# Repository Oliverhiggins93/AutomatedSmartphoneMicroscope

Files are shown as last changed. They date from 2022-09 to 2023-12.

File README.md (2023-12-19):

# AutomatedSmartphoneMicroscopeForDiagnosisOfHelminths

This is the github repo corresponding to the PhD thesis of Oliver Higgins "Deep-learning-assisted portable microscopy for disease diagnosis in low-resource settings". 

The project concerns the creation of a smartphone controlled portable microscope, which was used to detect Helminth eggs in faecal smears. The micrscope app includes an EfficientDet-based object detection algorithm which detects the eggs of the six most common spcies of helminth in images.

# Documentation 

Documentation for building the hardware and using the software is available at: https://oliverhiggins93.github.io/AutomatedSmartphoneMicroscope/

# Dataset 

A dataset of over 12,000 images of Helminth eggs was created as part of this project. The dataset includes images taken with standard brightfield microscopes (10x, 20x and 40 objectives) and the portable automated microscope (10x objective). The annotations were made in PASCAL VOC format and confirmed by staff at the Ministry of Health Uganda, Vector Control Division in Kampala. The dataset is available on Kaggle:

Dataset: https://www.kaggle.com/datasets/oliverjackhiggins/helminth-image-dataset

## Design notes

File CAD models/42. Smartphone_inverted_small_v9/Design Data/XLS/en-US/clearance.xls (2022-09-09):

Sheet: Ansi Unified Screw Threads
I | Sort Order -1
Fastener Type | Size | Shaft Diameters |  |  | Head Dimensions
 |  | Close | Normal | Loose | Diameter | Depth/Angle | Head Type
Flat Head Machine Screw (82) | #0 | 0.0635 | 0.07 | 0.073 | 0.119 | 82 | 2
Flat Head Machine Screw (82) | #1 | 0.076 | 0.081 | 0.089 | 0.146 | 82 | 2
Flat Head Machine Screw (82) | #2 | 0.089 | 0.096 | 0.1065 | 0.172 | 82 | 2
Flat Head Machine Screw (82) | #3 | 0.104 | 0.11 | 0.12 | 0.199 | 82 | 2
Flat Head Machine Screw (82) | #4 | 0.116 | 0.1285 | 0.136 | 0.225 | 82 | 2
Flat Head Machine Screw (82) | #5 | 0.1285 | 0.136 | 0.154 | 0.252 | 82 | 2
Flat Head Machine Screw (82) | #6 | 0.144 | 0.1495 | 0.1695 | 0.279 | 82 | 2
Flat Head Machine Screw (82) | #8 | 0.1695 | 0.177 | 0.1935 | 0.332 | 82 | 2
Flat Head Machine Screw (82) | #10 | 0.196 | 0.201 | 0.221 | 0.385 | 82 | 2
Flat Head Machine Screw (82) | #12 | 0.221 | 0.228 | 0.246 | 0.438 | 82 | 2
Flat Head Machine Screw (82) | 1/4 | 0.257 | 0.266 | 0.2812 | 0.507 | 82 | 2
Flat Head Machine Screw (82) | 5/16 | 0.323 | 0.332 | 0.3437 | 0.635 | 82 | 2
Flat Head Machine Screw (82) | 3/8 | 0.386 | 0.397 | 0.4062 | 0.762 | 82 | 2
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

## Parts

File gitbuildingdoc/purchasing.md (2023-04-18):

[M6x130 screws]:Parts.yaml#M3x8PanSteel
[M3x30 screws]:Parts.yaml#M3x8PanSteel
[M3x8 screws]:Parts.yaml#M3x8PanSteel
[M4x10 screws]:Parts.yaml#M4x10PanSteel
[No. 2 Phillips screwdriver]:Parts.yaml#Screwdriver_Philips_No2
[28BYJ-48]:Parts.yaml#28BYJ-48
[ULN2003]:Parts.yaml#ULN2003
[No. 2 Phillips screwdriver]:Parts.yaml#Screwdriver_Philips_No2

# Purchasing parts

The microscope contains quite a few parts which are not printed. The majority of these parts are bolts and motors which can be purchased in sets on Amazon or eBay. Currently there are lots of bolts needed for the microscope - in future iterations the number of bolts may be reduced. 

The Raspberry Pi Zero 2 is currently (as of 2022) difficult to acquire. If you cannot find one, you can get away with using the Raspberry Pi Zero, although the framerate will be slightly slower to stream to the smartphone. 

##Bolts

* [M3x8 bolts]: For fixing the Raspberry Pi, motors and motor boards to the microscope 
* [M4x10 bolts]: For fixing various parts of the stage together
* [M3x30 bolts]: Used for Z-travel
* [M6x130 bolts]: Used for X and Y travel

##Motor electronics
* 3x [28BYJ-48] Stepper motors
* 3x [ULN2003] Motor driver board

##LED electronics
* 1W White Star LED
* 100 Ohm resistor

##Raspberry Pi and camera
* Raspberry Pi HQ camera module
* Raspberry Pi
* 5V Power bank
* USB cable for power bank

##Optics
* 13mm diameter, 5mm focal length plastic condenser lens
* RMS objective
* Achromatic doublet tube lens (optional)

##Smartphone
* This should be any modern Android smartphone

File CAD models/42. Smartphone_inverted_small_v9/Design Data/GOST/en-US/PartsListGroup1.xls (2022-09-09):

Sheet: Лист 1
Инв. № подл |  |  |  | Подп. и дата | Взам. инв. № | Инв. № дубл. |  |  | Подп. и дата
Формат | Зона | Поз. | Обозначение |  |  |  | Наименование |  |  |  |  |  | Кол. на исполнение
 |  |  |  |  |  |  |  |  |  |  |  | Лит.
 |  |  |  |  |  |  |  |  |  |  |  | Код
 |  |  |  |  |  |  |  | Изм. | Лист | № докум | Подпись |  | Дата
 |  |  |  |  |  |  |  | Разраб.
 |  |  |  |  |  |  |  | Пров.
 |  |  |  |  |  |  |  | Н.контр
 |  |  |  |  |  |  |  | Утв.
 |  |  |  |  |  |  |  |  |  |  |  |  |  | Копировал

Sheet: Лист 2
Инв. № подл |  |  |  | Подп. и дата | Взам. инв. № | Инв. № дубл. |  |  | Подп. и дата
Формат | Зона | Поз. | Обозначение |  |  |  | Наименование |  |  |  |  | Кол. на исполнение
 |  |  |  |  |  |  |  | Изм. | Лист | № докум. | Подп. | Дата
 |  |  |  |  |  |  |  |  |  |  |  |  | Копировал
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

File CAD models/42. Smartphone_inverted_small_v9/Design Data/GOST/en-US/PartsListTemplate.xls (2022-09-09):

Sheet: Лист 1
 | Формат | Зона |  | Поз. |  | Обозначение |  |  |  | Наименование |  |  |  | Кол. | Приме-чание
Подп. и дата
Инв. № дубл.
Взам. инв. №
Подп. и дата
 | Изм. |  | Лист |  | № докум |  | Подпись | Дата
Инв. № подл | Разраб. |  |  |  |  |  |  |  |  |  | Литера |  | Лист |  |  | Листов
 | Пров.
 | Н.контр
 | Утв.
 |  |  |  |  |  |  |  |  | Копировал |  |  | Формат А4

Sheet: Лист 2
 | Формат | Зона |  | Поз. |  | Обозначение |  |  |  | Наименование |  | Кол. | Приме-чание
Подп. и дата
Инв. № дубл.
Взам. инв. №
Подп. и дата
Инв. № подл
 | Изм. |  | Лист |  | № докум. |  | Подп. |  | Дата
 |  |  |  |  |  |  |  | Копировал |  |  | Формат А4
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

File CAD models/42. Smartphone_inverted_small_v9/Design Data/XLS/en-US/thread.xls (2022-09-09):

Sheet: Inch Tapping Threads
I Q X | Inch Tapping Threads |  | Sort Order - 5 |  | External |  |  |  |  |  |  | Internal
 |  |  |  |  |  | Major Dia |  | Pitch Dia |  | Minor Dia |  |  | Minor Dia |  | Pitch Dia |  | Major Dia |  | Tap Drill
Size | Size Suffix | Thread Designation | Custom Thread Designation | TPI | Class | Max | Min | Max | Min | Max | Min | Class | Min | Max | Min | Max | Min | Max | Basic
0.0600 |  | 0-48 | 0-48 | 48 | 2B | 0.0600 | 0.0540 | 0.0480 | 0.0435 | 0.0360 | 0.0330
0.0730 |  | 1-42 | 1-42 | 42 | 2B | 0.0750 | 0.0690 | 0.0620 | 0.0575 | 0.0490 | 0.0460
0.0860 |  | 2-32 | 2-32 | 32 | 2B | 0.0880 | 0.0820 | 0.0760 | 0.0710 | 0.0640 | 0.0600
0.0990 |  | 3-28 | 3-28 | 28 | 2B | 0.1010 | 0.0950 | 0.0880 | 0.0830 | 0.0750 | 0.0710
0.1120 |  | 4-24 | 4-24 | 24 | 2B | 0.1140 | 0.1080 | 0.1000 | 0.0950 | 0.0860 | 0.0820
0.1250 |  | 5-20 | 5-20 | 20 | 2B | 0.1300 | 0.1230 | 0.1120 | 0.1065 | 0.0940 | 0.0900
0.1380 |  | 6-20 | 6-20 | 20 | 2B | 0.1390 | 0.1320 | 0.1215 | 0.1155 | 0.1040 | 0.0990
0.1510 |  | 7-19 | 7-19 | 19 | 2B | 0.1540 | 0.1470 | 0.1345 | 0.1280 | 0.1150 | 0.1090
0.1640 |  | 8-18 | 8-18 | 18 | 2B | 0.1660 | 0.1590 | 0.1440 | 0.1375 | 0.1220 | 0.1160
0.1900 |  | 10-16 | 10-16 | 16 | 2B | 0.1890 | 0.1820 | 0.1650 | 0.1585 | 0.1410 | 0.1350
0.2160 |  | 12-14 | 12-14 | 14 | 2B | 0.2150 | 0.2080 | 0.1895 | 0.1825 | 0.1640 | 0.1570
0.2420 |  | 14-14 | 14-14 | 14 | 2B | 0.2410 | 0.2340 | 0.2130 | 0.2060 | 0.1850 | 0.1780
0.2500 |  | 1/4-14 | 1/4-14 | 14 | 2B | 0.2460 | 0.2370 | 0.2190 | 0.2110 | 0.1920 | 0.1850
0.3125 |  | 5/16-12 | 5/16-12 | 12 | 2B | 0.3150 | 0.3060 | 0.2795 | 0.2710 | 0.2440 | 0.2360
0.3750 |  | 3/8-12 | 3/8-12 | 12 | 2B | 0.3800 | 0.3710 | 0.3445 | 0.3350 | 0.3090 | 0.2990
0.4375 |  | 7/16-10 | 7/16-10 | 10 | 2B | 0.4400 | 0.4290 | 0.3995 | 0.3890 | 0.3590 | 0.3490
0.5000 |  | 1/2-10 | 1/2-10 | 10 | 2B | 0.5040 | 0.4930 | 0.4635 | 0.4530 | 0.4230 | 0.4130

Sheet: Metric Forming Screw Threads
M P X | Metric Forming Screw Threads |  | Sort Order - 6 |  | External |  |  |  |  |  |  | Internal
 |  |  |  |  |  | Major Dia |  | Pitch Dia |  | Minor Dia |  |  | Minor Dia |  | Pitch Dia |  | Major Dia |  | Tap Drill
Size | Size Suffix | Thread Designation | Custom Thread Designation | Pitch | Class | Max | Min | Max | Min | Max | Min | Class | Min | Max | Min | Max | Min | Max | Basic
1.5 |  | 1.5x0.5 | 1.5x0.5 | 0.5 | 6g | 1.520 | 1.380 | 1.215 | 1.110 | 0.910 | 0.840
1.5 |  | ST1.5x0.5 | ST1.5x0.5 | 0.5 | 6g | 1.520 | 1.380 | 1.215 | 1.110 | 0.910 | 0.840
1.9 |  | 1.9x0.6 | 1.9x0.6 | 0.6 | 6g | 1.900 | 1.760 | 1.570 | 1.465 | 1.240 | 1.170
1.9 |  | ST1.9x0.6 | ST1.9x0.6 | 0.6 | 6g | 1.900 | 1.760 | 1.570 | 1.465 | 1.240 | 1.170
2.2 |  | 2.2x0.8 | 2.2x0.8 | 0.8 | 6g | 2.240 | 2.100 | 1.935 | 1.810 | 1.630 | 1.520
2.2 |  | ST2.2x0.8 | ST2.2x0.8 | 0.8 | 6g | 2.240 | 2.100 | 1.935 | 1.810 | 1.630 | 1.520
2.6 |  | 2.6x0.9 | 2.6x0.9 | 0.9 | 6g | 2.570 | 2.430 | 2.235 | 2.115 | 1.900 | 1.800
2.6 |  | ST2.6x0.9 | ST2.6x0.9 | 0.9 | 6g | 2.570 | 2.430 | 2.235 | 2.115 | 1.900 | 1.800
2.9 |  | 2.9x1 | 2.9x1 | 1 | 6g | 2.900 | 2.760 | 2.540 | 2.420 | 2.180 | 2.080
2.9 |  | 2.9x1.1 | 2.9x1.1 | 1.1 | 6g | 2.900 | 2.760 | 2.540 | 2.420 | 2.180 | 2.080
2.9 |  | ST2.9x1.1 | ST2.9x1.1 | 1.1 | 6g | 2.900 | 2.760 | 2.540 | 2.420 | 2.180 | 2.080
2.9 |  | 2.9x1.3 | 2.9x1.3 | 1.3 | 6g | 2.900 | 2.720 | 2.540 | 2.355 | 1.890 | 1.700
2.9 |  | 2.9x1.4 | 2.9x1.4 | 1.4 | 6g | 2.900 | 2.720 | 2.340 | 2.175 | 1.780 | 1.630
3.3 |  | 3.3x1.3 | 3.3x1.3 | 1.3 | 6g | 3.300 | 3.120 | 2.795 | 2.665 | 2.290 | 2.210
3.3 |  | ST3.3x1.3 | ST3.3x1.3 | 1.3 | 6g | 3.300 | 3.120 | 2.795 | 2.665 | 2.290 | 2.210
3.5 |  | 3.5x1.3 | 3.5x1.3 | 1.3 | 6g | 3.530 | 3.350 | 3.085 | 2.930 | 2.640 | 2.510
3.5 |  | ST3.5x1.3 | ST3.5x1.3 | 1.3 | 6g | 3.530 | 3.350 | 3.085 | 2.930 | 2.640 | 2.510
3.5 |  | 3.5x1.6 | 3.5x1.6 | 1.6 | 6g | 3.530 | 3.350 | 2.920 | 2.755 | 2.310 | 2.160
3.5 |  | 3.5x3.2 | 3.5x3.2 | 3.2 | 6g | 3.530 | 3.310 | 2.800 | 2.600 | 2.070 | 1.890
3.9 |  | 3.9x1.3 | 3.9x1.3 | 1.3 | 6g | 3.910 | 3.730 | 3.415 | 3.250 | 2.920 | 2.770
3.9 |  | ST3.9x1.3 | ST3.9x1.3 | 1.3 | 6g | 3.910 | 3.730 | 3.415 | 3.250 | 2.920 | 2.770
3.9 |  | 3.9x1.6 | 3.9x1.6 | 1.6 | 6g | 3.910 | 3.730 | 3.300 | 3.135 | 2.690 | 2.540
3.9 |  | 3.9x3.2 | 3.9x3.2 | 3.2 | 6g | 3.910 | 3.690 | 3.180 | 2.980 | 2.450 | 2.270
4.2 |  | 4.2x1.4 | 4.2x1.4 | 1.4 | 6g | 4.220 | 4.040 | 3.660 | 3.495 | 3.100 | 2.950
4.2 |  | ST4.2x1.4 | ST4.2x1.4 | 1.4 | 6g | 4.220 | 4.040 | 3.660 | 3.495 | 3.100 | 2.950
4.2 |  | 4.2x1.6 | 4.2x1.6 | 1.6 | 6g | 4.220 | 4.040 | 3.610 | 3.445 | 3.000 | 2.850
4.2 |  | 4.2x3.2 | 4.2x3.2 | 3.2 | 6g | 4.220 | 4.000 | 3.380 | 3.180 | 2.540 | 2.360
4.8 |  | 4.8x1.6 | 4.8x1.6 | 1.6 | 6g | 4.800 | 4.620 | 4.190 | 4.025 | 3.580 | 3.430
4.8 |  | ST4.8x1.6 | ST4.8x1.6 | 1.6 | 6g | 4.800 | 4.620 | 4.190 | 4.025 | 3.580 | 3.430
4.8 |  | 4.8x1.8 | 4.8x1.8 | 1.8 | 6g | 4.800 | 4.620 | 4.065 | 3.885 | 3.330 | 3.150
4.8 |  | 4.8x3.2 | 4.8x3.2 | 3.2 | 6g | 4.800 | 4.580 | 3.960 | 3.760 | 3.120 | 2.940
5.5 |  | 5.5x1.8 | 5.5x1.8 | 1.8 | 6g | 5.460 | 5.280 | 4.815 | 4.635 | 4.170 | 3.990
5.5 |  | ST5.5x1.8 | ST5.5x1.8 | 1.8 | 6g | 5.460 | 5.280 | 4.815 | 4.635 | 4.170 | 3.990
6.3 |  | 6.3x1.8 | 6.3x1.8 | 1.8 | 6g | 6.250 | 6.030 | 5.565 | 5.365 | 4.880 | 4.700
6.3 |  | ST6.3x1.8 | ST6.3x1.8 | 1.8 | 6g | 6.250 | 6.030 | 5.565 | 5.365 | 4.880 | 4.700
8.0 |  | 8x2.1 | 8x2.1 | 2.1 | 6g | 8.000 | 7.780 | 7.100 | 6.885 | 6.200 | 5.990
8.0 |  | ST8x2.1 | ST8x2.1 | 2.1 | 6g | 8.000 | 7.780 | 7.100 | 6.885 | 6.200 | 5.990
9.5 |  | 9.5x2.1 | 9.5x2.1 | 2.1 | 6g | 9.650 | 9.430 | 8.750 | 8.510 | 7.850 | 7.590
9.5 |  | ST9.5x2.1 | ST9.5x2.1 | 2.1 | 6g | 9.650 | 9.430 | 8.750 | 8.510 | 7.850 | 7.590

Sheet: ISO Pipe Threads
M Q | ISO Pipe Threads |  | Sort Order - 9 |  | External |  |  |  |  |  |  | Internal
 |  |  |  |  |  | Major Dia |  | Pitch Dia |  | Minor Dia |  |  | Minor Dia |  | Pitch Dia |  | Major Dia |  | Tap Drill | Thread Depth | Thread Runouts
Size | Size Suffix | Thread Designation | Custom Thread Designation | TPI | Class | Max | Min | Max | Min | Max | Min | Class | Min | Max | Min | Max | Min | Max | Basic
7.723 |  | G7.723x0.907 | G 1/16 | 28 | A | 7.723 | 7.509 | 7.142 | 7.035 | 6.561 |  |  | 6.561 | 6.834 | 7.142 | 7.249 | 7.723 |  | 1.5875 | 15.446 | 4.5000
7.723 |  | G7.723x0.907 | G 1/16 | 28 | B | 7.723 | 7.509 | 7.142 | 6.928 | 6.561
9.728 |  | G9.728x0.907 | G 1/8 | 28 | A | 9.728 | 9.514 | 9.147 | 9.040 | 8.566 |  |  | 8.566 | 8.848 | 9.147 | 9.254 | 9.728 |  | 3.1750 | 19.456 | 4.5000
9.728 |  | G9.728x0.907 | G 1/8 | 28 | B | 9.728 | 9.514 | 9.147 | 8.933 | 8.566
13.157 |  | G13.157x1.337 | G 1/4 | 19 | A | 13.157 | 12.907 | 12.301 | 12.176 | 11.445 |  |  | 11.445 | 11.89 | 12.301 | 12.426 | 13.157 |  | 6.3500 | 26.314 | 6.5000
13.157 |  | G13.157x1.337 | G 1/4 | 19 | B | 13.157 | 12.907 | 12.301 | 12.051 | 11.445
16.662 |  | G16.662x1.337 | G 3/8 | 19 | A | 16.662 | 16.412 | 15.806 | 15.681 | 14.950 |  |  | 14.95 | 15.395 | 15.806 | 15.931 | 16.662 |  | 9.5250 | 33.324 | 6.5000
16.662 |  | G16.662x1.337 | G 3/8 | 19 | B | 16.662 | 16.412 | 15.806 | 15.556 | 14.950
20.955 |  | G20.955x1.814 | G 1/2 | 14 | A | 20.955 | 20.671 | 19.793 | 19.651 | 18.631 |  |  | 18.631 | 19.172 | 19.793 | 19.935 | 20.955 |  | 12.7000 | 41.910 | 8.5000
20.955 |  | G20.955x1.814 | G 1/2 | 14 | B | 20.955 | 20.671 | 19.793 | 19.509 | 18.631
22.911 |  | G22.911x1.814 | G 5/8 | 14 | A | 22.911 | 22.627 | 21.749 | 21.607 | 20.587 |  |  | 20.587 | 21.128 | 21.749 | 21.891 | 22.911 |  |  | 45.822 | 8.5000
22.911 |  | G22.911x1.814 | G 5/8 | 14 | B | 22.911 | 22.627 | 21.749 | 21.465 | 20.587
26.441 |  | G26.441x1.814 | G 3/4 | 14 | A | 26.441 | 26.157 | 25.279 | 25.137 | 24.117 |  |  | 24.117 | 24.658 | 25.279 | 25.421 | 26.441 |  | 15.8750 | 52.882 | 8.5000
26.441 |  | G26.441x1.814 | G 3/4 | 14 | B | 26.441 | 26.157 | 25.279 | 24.995 | 24.117
30.201 |  | G30.201x1.814 | G 7/8 | 14 | A | 30.201 | 29.917 | 29.039 | 28.897 | 27.877 |  |  | 27.877 | 28.418 | 29.039 | 29.181 | 30.201 |  | 22.2250 | 60.402 | 8.5000
30.201 |  | G30.201x1.814 | G 7/8 | 14 | B | 30.201 | 29.917 | 29.039 | 28.755 | 27.877
33.249 |  | G33.249x2.309 | G 1 | 11 | A | 33.249 | 32.889 | 31.770 | 31.590 | 30.291 |  |  | 30.291 | 30.931 | 31.77 | 31.95 | 33.249 |  | 25.4000 | 66.498 | 10.0000
33.249 |  | G33.249x2.309 | G 1 | 11 | B | 33.249 | 32.889 | 31.770 | 31.410 | 30.291
37.897 |  | G37.897x2.309 | G 1 1/8 | 11 | A | 37.897 | 37.537 | 36.418 | 36.238 | 34.939 |  |  | 34.939 | 35.579 | 36.418 | 36.598 | 37.897 |  | 28.5750 | 75.794 | 10.0000
37.897 |  | G37.897x2.309 | G 1 1/8 | 11 | B | 37.897 | 37.537 | 36.418 | 36.058 | 34.939
41.910 |  | G41.91x2.309 | G 1 1/4 | 11 | A | 41.910 | 41.550 | 40.431 | 40.251 | 38.952 |  |  | 38.952 | 39.592 | 40.431 | 40.611 | 41.910 |  | 31.7500 | 83.820 | 10.0000
41.910 |  | G41.91x2.309 | G 1 1/4 | 11 | B | 41.910 | 41.550 | 40.431 | 40.071 | 38.952
47.803 |  | G47.803x2.309 | G 1 1/2 | 11 | A | 47.803 | 47.443 | 46.324 | 46.144 | 44.845 |  |  | 44.845 | 45.485 | 46.324 | 46.504 | 47.803 |  | 38.1000 | 95.606 | 10.0000
47.803 |  | G47.803x2.309 | G 1 1/2 | 11 | B | 47.803 | 47.443 | 46.324 | 45.964 | 44.845
53.746 |  | G53.746x2.309 | G 1 3/4 | 11 | A | 53.746 | 53.386 | 52.267 | 52.087 | 50.788 |  |  | 50.788 | 51.428 | 52.267 | 52.447 | 53.746 |  | 44.4500 | 107.492 | 10.0000
53.746 |  | G53.746x2.309 | G 1 3/4 | 11 | B | 53.746 | 53.386 | 52.267 | 51.907 | 50.788
59.614 |  | G59.614x2.309 | G 2 | 11 | A | 59.614 | 59.254 | 58.135 | 57.955 | 56.656 |  |  | 56.656 | 57.296 | 58.135 | 58.315 | 59.614 |  | 50.8000 | 119.228 | 10.0000
59.614 |  | G59.614x2.309 | G 2 | 11 | B | 59.614 | 59.254 | 58.135 | 57.775 | 56.656
65.710 |  | G65.71x2.309 | G 2 1/4 | 11 | A | 65.710 | 65.276 | 64.231 | 64.014 | 62.752 |  |  | 62.752 | 63.392 | 64.231 | 64.448 | 65.710 |  | 57.1500 | 131.420 | 10.0000
65.710 |  | G65.71x2.309 | G 2 1/4 | 11 | B | 65.710 | 65.276 | 64.231 | 63.797 | 62.752
75.184 |  | G75.184x2.309 | G 2 1/2 | 11 | A | 75.184 | 74.750 | 73.705 | 73.488 | 72.226 |  |  | 72.226 | 72.866 | 73.705 | 73.922 | 75.184 |  |  | 150.368 | 10.0000
75.184 |  | G75.184x2.309 | G 2 1/2 | 11 | B | 75.184 | 74.750 | 73.705 | 73.271 | 72.226
81.534 |  | G81.534x2.309 | G 2 3/4 | 11 | A | 81.534 | 81.100 | 80.055 | 79.838 | 78.576 |  |  | 78.576 | 79.216 | 80.055 | 80.272 | 81.534 |  | 69.8500 | 163.068 | 10.0000
81.534 |  | G81.534x2.309 | G 2 3/4 | 11 | B | 81.534 | 81.100 | 80.055 | 79.621 | 78.576
87.884 |  | G87.884x2.309 | G 3 | 11 | A | 87.884 | 87.450 | 86.405 | 86.188 | 84.926 |  |  | 84.926 | 85.566 | 86.405 | 86.622 | 87.884 |  | 76.2000 | 175.768 | 10.0000
87.884 |  | G87.884x2.309 | G 3 | 11 | B | 87.884 | 87.450 | 86.405 | 85.971 | 84.926
100.330 |  | G100.33x2.309 | G 3 1/2 | 11 | A | 100.330 | 99.896 | 98.851 | 98.634 | 97.372 |  |  | 97.372 | 98.012 | 98.851 | 99.068 | 100.330 |  | 88.9000 | 200.660 | 10.0000
100.330 |  | G100.33x2.309 | G 3 1/2 | 11 | B | 100.330 | 99.896 | 98.851 | 98.417 | 97.372
113.030 |  | G113.03x2.309 | G 4 | 11 | A | 113.030 | 112.596 | 111.551 | 111.334 | 110.072 |  |  | 110.072 | 110.712 | 111.551 | 111.768 | 113.030 |  | 101.6000 | 226.060 | 10.0000
113.030 |  | G113.03x2.309 | G 4 | 11 | B | 113.030 | 112.596 | 111.551 | 111.117 | 110.072
125.730 |  | G125.73x2.309 | G 4 1/2 | 11 | A | 125.730 | 125.296 | 124.251 | 124.034 | 122.772 |  |  | 122.772 | 123.412 | 124.251 | 124.468 | 125.730 |  | 114.3000 | 251.460 | 10.0000
125.730 |  | G125.73x2.309 | G 4 1/2 | 11 | B | 125.730 | 125.296 | 124.251 | 123.817 | 122.772
138.430 |  | G138.43x2.309 | G 5 | 11 | A | 138.430 | 137.996 | 136.951 | 136.734 | 135.472 |  |  | 135.472 | 136.112 | 136.951 | 137.168 | 138.430 |  | 127.0000 | 276.860 | 10.0000
138.430 |  | G138.43x2.309 | G 5 | 11 | B | 138.430 | 137.996 | 136.951 | 136.517 | 135.472
151.130 |  | G151.13x2.309 | G 5 1/2 | 11 | A | 151.130 | 150.696 | 149.651 | 149.434 | 148.172 |  |  | 148.172 | 148.812 | 149.651 | 149.868 | 151.130 |  | 139.7000 | 302.260 | 10.0000
151.130 |  | G151.13x2.309 | G 5 1/2 | 11 | B | 151.130 | 150.696 | 149.651 | 149.217 | 148.172
163.830 |  | G163.83x2.309 | G 6 | 11 | A | 163.830 | 163.396 | 162.351 | 162.134 | 160.872 |  |  | 160.872 | 161.512 | 162.351 | 162.568 | 163.830 |  | 152.4000 | 327.660 | 10.0000
163.830 |  | G163.83x2.309 | G 6 | 11 | B | 163.830 | 163.396 | 162.351 | 161.917 | 160.872

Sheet: JIS Pipe Threads
M Q | JIS Pipe Threads |  | Sort Order -12 |  | External |  |  |  |  |  |  | Internal
 |  |  |  |  |  | Major Dia |  | Pitch Dia |  | Minor Dia |  |  | Minor Dia |  | Pitch Dia |  | Major Dia |  | Tap Drill | Thread Depth | Thread Runouts
Size | Size Suffix | Thread Designation | Custom Thread Designation | TPI | Class | Max | Min | Max | Min | Max | Min | Class | Min | Max | Min | Max | Min | Max | Basic |  | Basic
7.723 |  | G7.723x0.907 | G 1/16 | 28 | A | 7.723 | 7.509 | 7.142 | 7.035 | 6.561 |  |  | 6.561 | 6.834 | 7.142 | 7.249 | 7.723 |  | 1.5875 | 15.446 | 4.5000
7.723 |  | G7.723x0.907 | G 1/16 | 28 | B | 7.723 | 7.509 | 7.142 | 6.928 | 6.561
9.728 |  | G9.728x0.907 | G 1/8 | 28 | A | 9.728 | 9.514 | 9.147 | 9.040 | 8.566 |  |  | 8.566 | 8.848 | 9.147 | 9.254 | 9.728 |  | 3.1750 | 19.456 | 4.5000
9.728 |  | G9.728x0.907 | G 1/8 | 28 | B | 9.728 | 9.514 | 9.147 | 8.933 | 8.566
13.157 |  | G13.157x1.337 | G 1/4 | 19 | A | 13.157 | 12.907 | 12.301 | 12.176 | 11.445 |  |  | 11.445 | 11.89 | 12.301 | 12.426 | 13.157 |  | 6.3500 | 26.314 | 6.5000
13.157 |  | G13.157x1.337 | G 1/4 | 19 | B | 13.157 | 12.907 | 12.301 | 12.051 | 11.445
16.662 |  | G16.662x1.337 | G 3/8 | 19 | A | 16.662 | 16.412 | 15.806 | 15.681 | 14.950 |  |  | 14.95 | 15.395 | 15.806 | 15.931 | 16.662 |  | 9.5250 | 33.324 | 6.5000
16.662 |  | G16.662x1.337 | G 3/8 | 19 | B | 16.662 | 16.412 | 15.806 | 15.556 | 14.950
20.955 |  | G20.955x1.814 | G 1/2 | 14 | A | 20.955 | 20.671 | 19.793 | 19.651 | 18.631 |  |  | 18.631 | 19.172 | 19.793 | 19.935 | 20.955 |  | 12.7000 | 41.910 | 8.5000
20.955 |  | G20.955x1.814 | G 1/2 | 14 | B | 20.955 | 20.671 | 19.793 | 19.509 | 18.631
22.911 |  | G22.911x1.814 | G 5/8 | 14 | A | 22.911 | 22.627 | 21.749 | 21.607 | 20.587 |  |  | 20.587 | 21.128 | 21.749 | 21.891 | 22.911 |  |  | 45.822 | 8.5000
22.911 |  | G22.911x1.814 | G 5/8 | 14 | B | 22.911 | 22.627 | 21.749 | 21.465 | 20.587
26.441 |  | G26.441x1.814 | G 3/4 | 14 | A | 26.441 | 26.157 | 25.279 | 25.137 | 24.117 |  |  | 24.117 | 24.658 | 25.279 | 25.421 | 26.441 |  | 15.8750 | 52.882 | 8.5000
26.441 |  | G26.441x1.814 | G 3/4 | 14 | B | 26.441 | 26.157 | 25.279 | 24.995 | 24.117
30.201 |  | G30.201x1.814 | G 7/8 | 14 | A | 30.201 | 29.917 | 29.039 | 28.897 | 27.877 |  |  | 27.877 | 28.418 | 29.039 | 29.181 | 30.201 |  | 22.2250 | 60.402 | 8.8000
30.201 |  | G30.201x1.814 | G 7/8 | 14 | B | 30.201 | 29.917 | 29.039 | 28.755 | 27.877
33.249 |  | G33.249x2.309 | G 1 | 11 | A | 33.249 | 32.889 | 31.770 | 31.590 | 30.291 |  |  | 30.291 | 30.931 | 31.77 | 31.95 | 33.249 |  | 25.4000 | 66.498 | 10.0000
33.249 |  | G33.249x2.309 | G 1 | 11 | B | 33.249 | 32.889 | 31.770 | 31.410 | 30.291
37.897 |  | G37.897x2.309 | G 1 1/8 | 11 | A | 37.897 | 37.537 | 36.418 | 36.238 | 34.939 |  |  | 34.939 | 35.579 | 36.418 | 36.598 | 37.897 |  | 28.5750 | 75.794 | 10.0000
37.897 |  | G37.897x2.309 | G 1 1/8 | 11 | B | 37.897 | 37.537 | 36.418 | 36.058 | 34.939
41.910 |  | G41.91x2.309 | G 1 1/4 | 11 | A | 41.910 | 41.550 | 40.431 | 40.251 | 38.952 |  |  | 38.952 | 39.592 | 40.431 | 40.611 | 41.910 |  | 31.7500 | 83.820 | 10.0000
41.910 |  | G41.91x2.309 | G 1 1/4 | 11 | B | 41.910 | 41.550 | 40.431 | 40.071 | 38.952
47.803 |  | G47.803x2.309 | G 1 1/2 | 11 | A | 47.803 | 47.443 | 46.324 | 46.144 | 44.845 |  |  | 44.845 | 45.485 | 46.324 | 46.504 | 47.803 |  | 38.1000 | 95.606 | 10.0000
47.803 |  | G47.803x2.309 | G 1 1/2 | 11 | B | 47.803 | 47.443 | 46.324 | 45.964 | 44.845
53.746 |  | G53.746x2.309 | G 1 3/4 | 11 | A | 53.746 | 53.386 | 52.267 | 52.087 | 50.788 |  |  | 50.788 | 51.428 | 52.267 | 52.447 | 53.746 |  | 44.4500 | 107.492 | 10.0000
53.746 |  | G53.746x2.309 | G 1 3/4 | 11 | B | 53.746 | 53.386 | 52.267 | 51.907 | 50.788
59.614 |  | G59.614x2.309 | G 2 | 11 | A | 59.614 | 59.254 | 58.135 | 57.955 | 56.656 |  |  | 56.656 | 57.296 | 58.135 | 58.315 | 59.614 |  | 50.8000 | 119.228 | 10.0000
59.614 |  | G59.614x2.309 | G 2 | 11 | B | 59.614 | 59.254 | 58.135 | 57.775 | 56.656
65.710 |  | G65.71x2.309 | G 2 1/4 | 11 | A | 65.710 | 65.276 | 64.231 | 64.014 | 62.752 |  |  | 62.752 | 63.392 | 64.231 | 64.448 | 65.710 |  | 57.1500 | 131.420 | 10.0000
65.710 |  | G65.71x2.309 | G 2 1/4 | 11 | B | 65.710 | 65.276 | 64.231 | 63.797 | 62.752
75.184 |  | G75.184x2.309 | G 2 1/2 | 11 | A | 75.184 | 74.750 | 73.705 | 73.488 | 72.226 |  |  | 72.226 | 72.866 | 73.705 | 73.922 | 75.184 |  |  | 150.368 | 10.0000
75.184 |  | G75.184x2.309 | G 2 1/2 | 11 | B | 75.184 | 74.750 | 73.705 | 73.271 | 72.226
81.534 |  | G81.534x2.309 | G 2 3/4 | 11 | A | 81.534 | 81.100 | 80.055 | 79.838 | 78.576 |  |  | 78.576 | 79.216 | 80.055 | 80.272 | 81.534 |  | 69.8500 | 163.068 | 10.0000
81.534 |  | G81.534x2.309 | G 2 3/4 | 11 | B | 81.534 | 81.100 | 80.055 | 79.621 | 78.576
87.884 |  | G87.884x2.309 | G 3 | 11 | A | 87.884 | 87.450 | 86.405 | 86.188 | 84.926 |  |  | 84.926 | 85.566 | 86.405 | 86.622 | 87.884 |  | 76.2000 | 175.768 | 10.0000
87.884 |  | G87.884x2.309 | G 3 | 11 | B | 87.884 | 87.450 | 86.405 | 85.971 | 84.926
100.330 |  | G100.33x2.309 | G 3 1/2 | 11 | A | 100.330 | 99.896 | 98.851 | 98.634 | 97.372 |  |  | 97.372 | 98.012 | 98.851 | 99.068 | 100.330 |  | 88.9000 | 200.660 | 10.0000
100.330 |  | G100.33x2.309 | G 3 1/2 | 11 | B | 100.330 | 99.896 | 98.851 | 98.417 | 97.372
113.030 |  | G113.03x2.309 | G 4 | 11 | A | 113.030 | 112.596 | 111.551 | 111.334 | 110.072 |  |  | 110.072 | 110.712 | 111.551 | 111.768 | 113.030 |  | 101.6000 | 226.060 | 10.0000
113.030 |  | G113.03x2.309 | G 4 | 11 | B | 113.030 | 112.596 | 111.551 | 111.117 | 110.072
125.730 |  | G125.73x2.309 | G 4 1/2 | 11 | A | 125.730 | 125.296 | 124.251 | 124.034 | 122.772 |  |  | 122.772 | 123.412 | 124.251 | 124.468 | 125.730 |  | 114.3000 | 251.460 | 10.0000
125.730 |  | G125.73x2.309 | G 4 1/2 | 11 | B | 125.730 | 125.296 | 124.251 | 123.817 | 122.772
138.430 |  | G138.43x2.309 | G 5 | 11 | A | 138.430 | 137.996 | 136.951 | 136.734 | 135.472 |  |  | 135.472 | 136.112 | 136.951 | 137.168 | 138.430 |  | 127.0000 | 276.860 | 10.0000
138.430 |  | G138.43x2.309 | G 5 | 11 | B | 138.430 | 137.996 | 136.951 | 136.517 | 135.472
151.130 |  | G151.13x2.309 | G 5 1/2 | 11 | A | 151.130 | 150.696 | 149.651 | 149.434 | 148.172 |  |  | 148.172 | 148.812 | 149.651 | 149.868 | 151.130 |  | 139.7000 | 302.260 | 10.0000
151.130 |  | G151.13x2.309 | G 5 1/2 | 11 | B | 151.130 | 150.696 | 149.651 | 149.217 | 148.172
163.830 |  | G163.83x2.309 | G 6 | 11 | A | 163.830 | 163.396 | 162.351 | 162.134 | 160.872 |  |  | 160.872 | 161.512 | 162.351 | 162.568 | 163.830 |  | 152.4000 | 327.660 | 10.0000
163.830 |  | G163.83x2.309 | G 6 | 11 | B | 163.830 | 163.396 | 162.351 | 161.917 | 160.872

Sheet: DIN Pipe Threads
M Q | DIN Pipe Threads |  | Sort Order - 18 |  | External |  |  |  |  |  |  | Internal
 |  |  |  |  |  | Major Dia |  | Pitch Dia |  | Minor Dia |  |  | Minor Dia |  | Pitch Dia |  | Major Dia |  | Tap Drill | Thread Depth | Thread Runouts
Size | Size Suffix | Thread Designation | Custom Thread Designation | TPI | Class | Max | Min | Max | Min | Max | Min | Class | Min | Max | Min | Max | Min | Max | Basic
7.723 |  | G7.723x0.907 | G 1/16 | 28 | A | 7.723 | 7.509 | 7.142 | 7.035 | 6.561 |  |  | 6.561 | 6.834 | 7.142 | 7.249 | 7.723 |  | 1.5875 | 15.446 | 4.5000
7.723 |  | G7.723x0.907 | G 1/16 | 28 | B | 7.723 | 7.509 | 7.142 | 6.928 | 6.561
9.728 |  | G9.728x0.907 | G 1/8 | 28 | A | 9.728 | 9.514 | 9.147 | 9.040 | 8.566 |  |  | 8.566 | 8.848 | 9.147 | 9.254 | 9.728 |  | 3.1750 | 19.456 | 4.5000
9.728 |  | G9.728x0.907 | G 1/8 | 28 | B | 9.728 | 9.514 | 9.147 | 8.933 | 8.566
13.157 |  | G13.157x1.337 | G 1/4 | 19 | A | 13.157 | 12.907 | 12.301 | 12.176 | 11.445 |  |  | 11.445 | 11.89 | 12.301 | 12.426 | 13.157 |  | 6.3500 | 26.314 | 6.5000
13.157 |  | G13.157x1.337 | G 1/4 | 19 | B | 13.157 | 12.907 | 12.301 | 12.051 | 11.445
16.662 |  | G16.662x1.337 | G 3/8 | 19 | A | 16.662 | 16.412 | 15.806 | 15.681 | 14.950 |  |  | 14.95 | 15.395 | 15.806 | 15.931 | 16.662 |  | 9.5250 | 33.324 | 6.5000
16.662 |  | G16.662x1.337 | G 3/8 | 19 | B | 16.662 | 16.412 | 15.806 | 15.556 | 14.950
20.955 |  | G20.955x1.814 | G 1/2 | 14 | A | 20.955 | 20.671 | 19.793 | 19.651 | 18.631 |  |  | 18.631 | 19.172 | 19.793 | 19.935 | 20.955 |  | 12.7000 | 41.910 | 8.5000
20.955 |  | G20.955x1.814 | G 1/2 | 14 | B | 20.955 | 20.671 | 19.793 | 19.509 | 18.631
22.911 |  | G22.911x1.814 | G 5/8 | 14 | A | 22.911 | 22.627 | 21.749 | 21.607 | 20.587 |  |  | 20.587 | 21.128 | 21.749 | 21.891 | 22.911 |  |  | 45.822 | 8.5000
22.911 |  | G22.911x1.814 | G 5/8 | 14 | B | 22.911 | 22.627 | 21.749 | 21.465 | 20.587
26.441 |  | G26.441x1.814 | G 3/4 | 14 | A | 26.441 | 26.157 | 25.279 | 25.137 | 24.117 |  |  | 24.117 | 24.658 | 25.279 | 25.421 | 26.441 |  | 15.8750 | 52.882 | 8.5000
26.441 |  | G26.441x1.814 | G 3/4 | 14 | B | 26.441 | 26.157 | 25.279 | 24.995 | 24.117
30.201 |  | G30.201x1.814 | G 7/8 | 14 | A | 30.201 | 29.917 | 29.039 | 28.897 | 27.877 |  |  | 27.877 | 28.418 | 29.039 | 29.181 | 30.201 |  | 22.2250 | 60.402 | 8.5000
30.201 |  | G30.201x1.814 | G 7/8 | 14 | B | 30.201 | 29.917 | 29.039 | 28.755 | 27.877
33.249 |  | G33.249x2.309 | G 1 | 11 | A | 33.249 | 32.889 | 31.770 | 31.590 | 30.291 |  |  | 30.291 | 30.931 | 31.77 | 31.95 | 33.249 |  | 25.4000 | 66.498 | 10.5000
33.249 |  | G33.249x2.309 | G 1 | 11 | B | 33.249 | 32.889 | 31.770 | 31.410 | 30.291
37.897 |  | G37.897x2.309 | G 1 1/8 | 11 | A | 37.897 | 37.537 | 36.418 | 36.238 | 34.939 |  |  | 34.939 | 35.579 | 36.418 | 36.598 | 37.897 |  | 28.5750 | 75.794 | 10.5000
37.897 |  | G37.897x2.309 | G 1 1/8 | 11 | B | 37.897 | 37.537 | 36.418 | 36.058 | 34.939
41.910 |  | G41.91x2.309 | G 1 1/4 | 11 | A | 41.910 | 41.550 | 40.431 | 40.251 | 38.952 |  |  | 38.952 | 39.592 | 40.431 | 40.611 | 41.910 |  | 31.7500 | 83.820 | 10.5000
41.910 |  | G41.91x2.309 | G 1 1/4 | 11 | B | 41.910 | 41.550 | 40.431 | 40.071 | 38.952
47.803 |  | G47.803x2.309 | G 1 1/2 | 11 | A | 47.803 | 47.443 | 46.324 | 46.144 | 44.845 |  |  | 44.845 | 45.485 | 46.324 | 46.504 | 47.803 |  | 38.1000 | 95.606 | 10.5000
47.803 |  | G47.803x2.309 | G 1 1/2 | 11 | B | 47.803 | 47.443 | 46.324 | 45.964 | 44.845
53.746 |  | G53.746x2.309 | G 1 3/4 | 11 | A | 53.746 | 53.386 | 52.267 | 52.087 | 50.788 |  |  | 50.788 | 51.428 | 52.267 | 52.447 | 53.746 |  | 44.4500 | 107.492 | 10.5000
53.746 |  | G53.746x2.309 | G 1 3/4 | 11 | B | 53.746 | 53.386 | 52.267 | 51.907 | 50.788
59.614 |  | G59.614x2.309 | G 2 | 11 | A | 59.614 | 59.254 | 58.135 | 57.955 | 56.656 |  |  | 56.656 | 57.296 | 58.135 | 58.315 | 59.614 |  | 50.8000 | 119.228 | 10.5000
59.614 |  | G59.614x2.309 | G 2 | 11 | B | 59.614 | 59.254 | 58.135 | 57.775 | 56.656
65.710 |  | G65.71x2.309 | G 2 1/4 | 11 | A | 65.710 | 65.276 | 64.231 | 64.014 | 62.752 |  |  | 62.752 | 63.392 | 64.231 | 64.448 | 65.710 |  | 57.1500 | 131.420 | 10.5000
65.710 |  | G65.71x2.309 | G 2 1/4 | 11 | B | 65.710 | 65.276 | 64.231 | 63.797 | 62.752
75.184 |  | G75.184x2.309 | G 2 1/2 | 11 | A | 75.184 | 74.750 | 73.705 | 73.488 | 72.226 |  |  | 72.226 | 72.866 | 73.705 | 73.922 | 75.184 |  |  | 150.368 | 10.5000
75.184 |  | G75.184x2.309 | G 2 1/2 | 11 | B | 75.184 | 74.750 | 73.705 | 73.271 | 72.226
81.534 |  | G81.534x2.309 | G 2 3/4 | 11 | A | 81.534 | 81.100 | 80.055 | 79.838 | 78.576 |  |  | 78.576 | 79.216 | 80.055 | 80.272 | 81.534 |  | 69.8500 | 163.068 | 10.5000
81.534 |  | G81.534x2.309 | G 2 3/4 | 11 | B | 81.534 | 81.100 | 80.055 | 79.621 | 78.576
87.884 |  | G87.884x2.309 | G 3 | 11 | A | 87.884 | 87.450 | 86.405 | 86.188 | 84.926 |  |  | 84.926 | 85.566 | 86.405 | 86.622 | 87.884 |  | 76.2000 | 175.768 | 10.5000
87.884 |  | G87.884x2.309 | G 3 | 11 | B | 87.884 | 87.450 | 86.405 | 85.971 | 84.926
100.330 |  | G100.33x2.309 | G 3 1/2 | 11 | A | 100.330 | 99.896 | 98.851 | 98.634 | 97.372 |  |  | 97.372 | 98.012 | 98.851 | 99.068 | 100.330 |  | 88.9000 | 200.660 | 10.5000
100.330 |  | G100.33x2.309 | G 3 1/2 | 11 | B | 100.330 | 99.896 | 98.851 | 98.417 | 97.372
113.030 |  | G113.03x2.309 | G 4 | 11 | A | 113.030 | 112.596 | 111.551 | 111.334 | 110.072 |  |  | 110.072 | 110.712 | 111.551 | 111.768 | 113.030 |  | 101.6000 | 226.060 | 10.5000
113.030 |  | G113.03x2.309 | G 4 | 11 | B | 113.030 | 112.596 | 111.551 | 111.117 | 110.072
125.730 |  | G125.73x2.309 | G 4 1/2 | 11 | A | 125.730 | 125.296 | 124.251 | 124.034 | 122.772 |  |  | 122.772 | 123.412 | 124.251 | 124.468 | 125.730 |  | 114.3000 | 251.460 | 10.5000
125.730 |  | G125.73x2.309 | G 4 1/2 | 11 | B | 125.730 | 125.296 | 124.251 | 123.817 | 122.772
138.430 |  | G138.43x2.309 | G 5 | 11 | A | 138.430 | 137.996 | 136.951 | 136.734 | 135.472 |  |  | 135.472 | 136.112 | 136.951 | 137.168 | 138.430 |  | 127.0000 | 276.860 | 10.5000
138.430 |  | G138.43x2.309 | G 5 | 11 | B | 138.430 | 137.996 | 136.951 | 136.517 | 135.472
151.130 |  | G151.13x2.309 | G 5 1/2 | 11 | A | 151.130 | 150.696 | 149.651 | 149.434 | 148.172 |  |  | 148.172 | 148.812 | 149.651 | 149.868 | 151.130 |  | 139.7000 | 302.260 | 10.5000
151.130 |  | G151.13x2.309 | G 5 1/2 | 11 | B | 151.130 | 150.696 | 149.651 | 149.217 | 148.172
163.830 |  | G163.83x2.309 | G 6 | 11 | A | 163.830 | 163.396 | 162.351 | 162.134 | 160.872 |  |  | 160.872 | 161.512 | 162.351 | 162.568 | 163.830 |  | 152.4000 | 327.660 | 10.5000
163.830 |  | G163.83x2.309 | G 6 | 11 | B | 163.830 | 163.396 | 162.351 | 161.917 | 160.872

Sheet: BSP Pipe Threads
M Q | BSP Pipe Threads |  | Sort Order - 19 |  | External |  |  |  |  |  |  | Internal
 |  |  |  |  |  | Major Dia |  | Pitch Dia |  | Minor Dia |  |  | Minor Dia |  | Pitch Dia |  | Major Dia |  | Tap Drill | Thread Depth | Thread Runouts
Size | Size Suffix | Thread Designation | Custom Thread Designation | TPI | Class | Max | Min | Max | Min | Max | Min | Class | Min | Max | Min | Max | Min | Max | Basic |  | Basic
1/16 |  | G 1/16-28 | G 1/16-28 | 28 | A | 7.723 | 7.509 | 7.142 | 7.035 | 6.561 |  |  | 6.561 | 6.834 | 7.142 | 7.249 | 7.723 |  | 6.6000 | 15.4460 | 4.5000
1/16 |  | G 1/16-28 | G 1/16-28 | 28 | B | 7.723 | 7.509 | 7.142 | 7.035 | 6.561
1/8 |  | G 1/8-28 | G 1/8-28 | 28 | A | 9.728 | 9.514 | 9.147 | 9.040 | 8.566 |  |  | 8.566 | 8.848 | 9.147 | 9.254 | 9.728 |  | 8.7300 | 19.4560 | 4.5000
1/8 |  | G 1/8-28 | G 1/8-28 | 28 | B | 9.728 | 9.514 | 9.147 | 9.040 | 8.566
1/4 |  | G 1/4-19 | G 1/4-19 | 19 | A | 13.157 | 12.907 | 12.301 | 12.176 | 11.445 |  |  | 11.445 | 11.89 | 12.301 | 12.426 | 13.157 |  | 11.8000 | 26.3140 | 6.5000
1/4 |  | G 1/4-19 | G 1/4-19 | 19 | B | 13.157 | 12.907 | 12.301 | 12.176 | 11.445
3/8 |  | G 3/8-19 | G 3/8-19 | 19 | A | 16.662 | 16.412 | 15.806 | 15.681 | 14.950 |  |  | 14.95 | 15.395 | 15.806 | 15.931 | 16.662 |  | 15.2500 | 33.3240 | 6.5000
3/8 |  | G 3/8-19 | G 3/8-19 | 19 | B | 16.662 | 16.412 | 15.806 | 15.681 | 14.950
1/2 |  | G 1/2-14 | G 1/2-14 | 14 | A | 20.955 | 20.671 | 19.793 | 19.651 | 18.631 |  |  | 18.631 | 19.172 | 19.793 | 19.935 | 20.955 |  | 19.0500 | 41.9100 | 8.5000
1/2 |  | G 1/2-14 | G 1/2-14 | 14 | B | 20.955 | 20.671 | 19.793 | 19.651 | 18.631
5/8 |  | G 5/8-14 | G 5/8-14 | 14 | A | 22.911 | 22.627 | 21.749 | 21.607 | 20.587 |  |  | 20.587 | 21.128 | 21.749 | 21.891 | 22.911 |  | 21.0000 | 45.8220 | 8.5000
5/8 |  | G 5/8-14 | G 5/8-14 | 14 | B | 22.911 | 22.627 | 21.749 | 21.607 | 20.587
3/4 |  | G 3/4-14 | G 3/4-14 | 14 | A | 26.441 | 26.157 | 25.279 | 25.137 | 24.117 |  |  | 24.117 | 24.658 | 25.279 | 25.421 | 26.441 |  | 24.5000 | 52.8820 | 8.5000
3/4 |  | G 3/4-14 | G 3/4-14 | 14 | B | 26.441 | 26.157 | 25.279 | 25.137 | 24.117
7/8 |  | G 7/8-14 | G 7/8-14 | 14 | A | 30.201 | 29.917 | 29.039 | 28.897 | 27.877 |  |  | 27.877 | 28.418 | 29.039 | 29.181 | 30.201 |  | 28.2500 | 60.4020 | 8.5000
7/8 |  | G 7/8-14 | G 7/8-14 | 14 | B | 30.201 | 29.917 | 29.039 | 28.897 | 27.877
1 |  | G 1-11 | G 1-11 | 11 | A | 33.249 | 32.889 | 31.770 | 31.590 | 30.291 |  |  | 30.291 | 30.931 | 31.77 | 31.95 | 33.249 |  | 30.7500 | 66.4980 | 10.0000
1 |  | G 1-11 | G 1-11 | 11 | B | 33.249 | 32.889 | 31.770 | 31.590 | 30.291
1 1/4 |  | G 1 1/4-11 | G 1 1/4-11 | 11 | A | 41.910 | 41.550 | 40.431 | 40.251 | 38.952 |  |  | 38.952 | 39.592 | 40.431 | 40.611 | 41.910 |  | 39.5000 | 83.8200 | 10.0000
1 1/4 |  | G 1 1/4-11 | G 1 1/4-11 | 11 | B | 41.910 | 41.550 | 40.431 | 40.251 | 38.952
1 1/2 |  | G 1 1/2-11 | G 1 1/2-11 | 11 | A | 47.803 | 47.443 | 46.324 | 46.144 | 44.845 |  |  | 44.845 | 45.485 | 46.324 | 46.504 | 47.803 |  | 45.5000 | 95.6060 | 10.0000
1 1/2 |  | G 1 1/2-11 | G 1 1/2-11 | 11 | B | 47.803 | 47.443 | 46.324 | 46.144 | 44.845
1 3/4 |  | G 1 3/4-11 | G 1 3/4-11 | 11 | A | 53.746 | 53.386 | 52.267 | 52.087 | 50.788 |  |  | 50.788 | 51.428 | 52.267 | 52.447 | 53.746 |  | 51.0000 | 107.4920 | 10.0000
1 3/4 |  | G 1 3/4-11 | G 1 3/4-11 | 11 | B | 53.746 | 53.386 | 52.267 | 52.087 | 50.788
2 |  | G 2-11 | G 2-11 | 11 | A | 59.614 | 59.254 | 58.135 | 57.955 | 56.656 |  |  | 56.656 | 57.296 | 58.135 | 58.315 | 59.614 |  | 57.0000 | 119.2280 | 10.0000
2 |  | G 2-11 | G 2-11 | 11 | B | 59.614 | 59.254 | 58.135 | 57.955 | 56.656
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

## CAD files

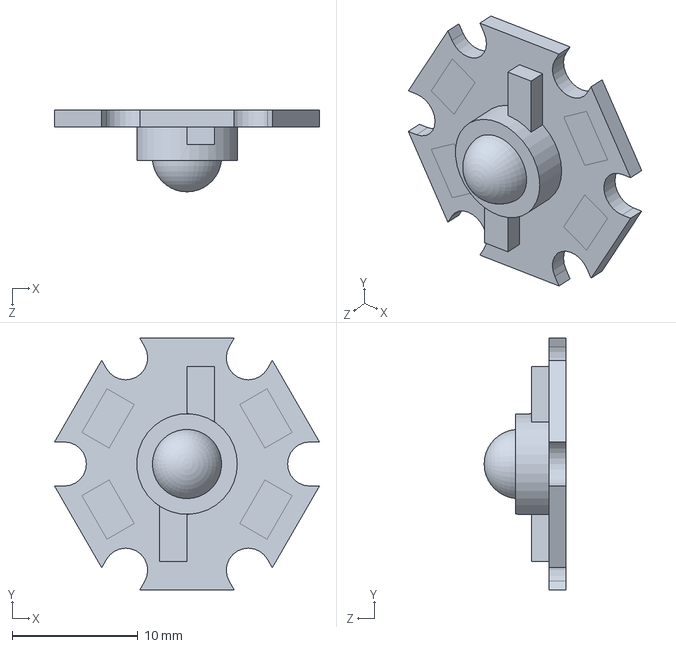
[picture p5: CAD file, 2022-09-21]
CAD models/42. Smartphone_inverted_small_v9/1W_star_LED.SLDPRT
21.1 x 20.0 x 6.50 mm

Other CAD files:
CAD models/42. Smartphone_inverted_small_v9/160mm_shunt_box.ipt
CAD models/42. Smartphone_inverted_small_v9/1W_star_LED.ipt
CAD models/42. Smartphone_inverted_small_v9/28BYJ-48 Stepper.ipt
CAD models/42. Smartphone_inverted_small_v9/3mm_shaft_couple_sideclip_v4.ipt
CAD models/42. Smartphone_inverted_small_v9/6mm_shaft_couple_sideclip_v2.ipt
CAD models/42. Smartphone_inverted_small_v9/AC127-075-A-Step.ipt
CAD models/42. Smartphone_inverted_small_v9/Bottom_carriage.ipt
CAD models/42. Smartphone_inverted_small_v9/Condenser_holder_frame.ipt
CAD models/42. Smartphone_inverted_small_v9/Flexible_cam_holder_v7_HQ.ipt
CAD models/42. Smartphone_inverted_small_v9/Flexible_tube_bolster_fixed_v3.ipt
CAD models/42. Smartphone_inverted_small_v9/Led_frame_2_4mm.ipt
CAD models/42. Smartphone_inverted_small_v9/Lensfree_flexstage_box.iam
CAD models/42. Smartphone_inverted_small_v9/M3 nut.ipt
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

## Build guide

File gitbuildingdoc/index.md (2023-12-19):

# Automated Smartphone Microscope

#Introduction

The following pages provide build and software instructions for the Automated Smartphone Microscope project. This project is a 3D printable microscope which can be controlled using an app installed on any Android smartphone. The microscope is motorised, has a large travel area, and can accept any RMS threaded objective. 

This page provides a few thoughts about the project, while the links below contain information about how to build the microscope and run the software. 

[Github page](https://github.com/Oliverhiggins93/AutomatedSmartphoneMicroscope)

<center>Printed microscope</center>

#Instructions

* [.](introduction.md){step}
* [Bill of materials]{BOM}
* [Purchasing parts](purchasing.md){step}
* [Printing parts](printing.md){step}
* [Assembling microscope](assembly.md){step}
* [Raspberry Pi Software](raspberrypi.md){step}
* [Android Software installation](androidinstallation.md){step}
* [App instructions](appinstructions.md){step}
* [Helminth dataset](dataset.md){step}

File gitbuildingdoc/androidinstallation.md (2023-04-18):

# Android app software

## Pair Raspberry Pi with phone {pagestep}

For starters you will need to make sure that the Raspberry Pi can connect to the smartphone's mobile hotspot. If you used the default SSID and password settings in the previous settings you should only need to change the smartphone's hotspot settings to match the ones that the Raspberry Pi will be expecting to connect to: 

* Network name (SSID) = microscope
* Password = smart 

Usually this can be done through settings. If you search for Mobile Hotspot in your device's search function it will usually take you to a page where you can switch the hotspot on and change the Network name/SSID and password.

You will want to check at this stage that the Raspberry Pi is connected to your mobile hotspot. Usually under the mobile hotspot settings there will be some information telling you which devices are connected. 

## Download Android Studio {pagestep}

Download and install Android Studio from the following website: [Android studio](https://developer.android.com/studio)

## Import app into android studio and install {pagestep}

Open Android Studio once it is downloaded and installed. 

If you have not yet cloned the repository, you will want to do that now using:

> git clone https://github.com/Oliverhiggins93/AutomatedSmartphoneMicroscope.git

In Android Studio, open the project by opening the File dropdown and selection Open 

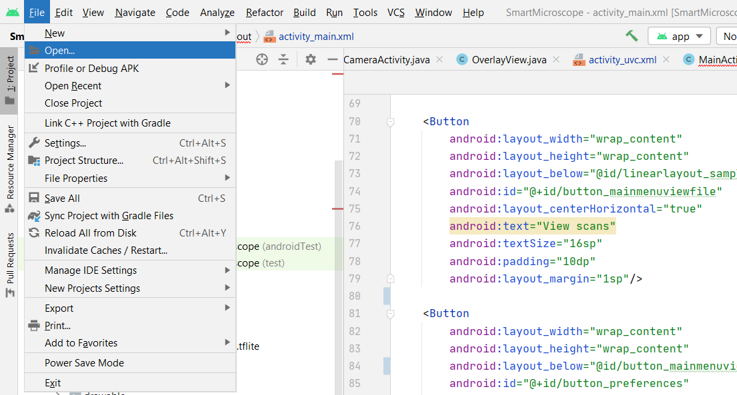
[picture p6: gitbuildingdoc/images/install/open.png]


You will need to open the folder entitled 'Smartmicroscope'.
 
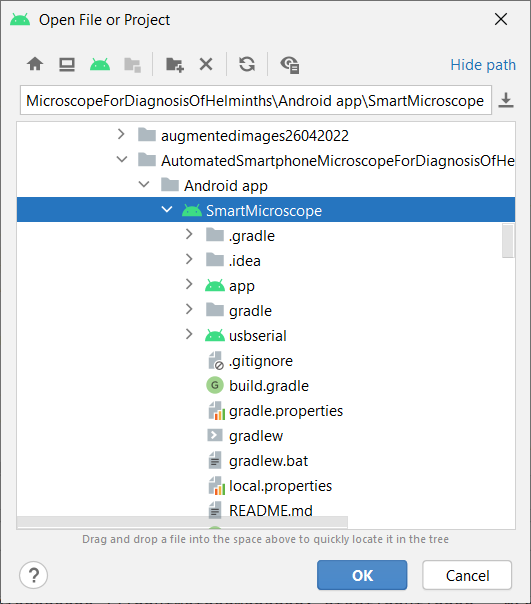
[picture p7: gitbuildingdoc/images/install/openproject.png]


Once this is open you should build and install the app. 

## Run app {pagestep}

You can now run the app from the phone. The most important thing to check at this stage is whether you can receive an image. By clicking on 'Open Web Camera' you should soon begin to see an image stream to your device.

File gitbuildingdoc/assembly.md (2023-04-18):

[Raspberry Pi]:Parts.yaml#RaspberyPi
[Raspberry Pi Camera]:Parts.yaml#RaspberyPiCamera
[M3 bolt]:Parts.yaml#M3x8PanSteel
[28BYJ-48]:Parts.yaml#28BYJ-48
[ULN2003]:Parts.yaml#ULN2003
[Jumper wires]:Parts.yaml#Jumperwires
[3mm bolt coupler]:Parts.yaml#Shaftcouple3mm
[6mm bolt coupler]:Parts.yaml#Shaftcouple6mm
[M3x30mm bolt]:Parts.yaml#M3x30GHexSteel
[M3x8mm bolt]:Parts.yaml#M3x8PanSteel
[M6x130mm bolt]:Parts.yaml#M6x130PanSteel
[M3 nut]:Parts.yaml#M3nut
[M6 nut]:Parts.yaml#M6nut
[M2.5x6mm bolt]:Parts.yaml#M2.5x6
[M4x10mm bolt]:Parts.yaml#M4x10PanSteel
[Condenser lens]:Parts.yaml#Plasticcondenser
[White LED]:Parts.yaml#1WLED
[Resistor]:Parts.yaml#resistor
[RMS objective]:Parts.yaml#rmsobjective
[Tube lens]:Parts.yaml#tubelens
[Camera ribbon]:Parts.yaml#RaspberyPiCameraRibbon

# Assembling the microscope 

## Attaching Raspberry pi and motor drivers to base {pagestep}

We will start by assembling the base of the microscope and attaching the electronic components. You will want to thread the bolts through the bottom of the base so that the threaded ends finish inside the microscopy body. 

Take the [Raspberry Pi]{Qty: 1} and thread an [M3 bolt]{Qty: 4} through the hole in each corners. Secure the [Raspberry Pi] with the bolts and 4x [M3 nut]{Qty: 4}.

Take the 3x [ULN2003]{Qty: 3} motor drivers and attach these to the base in the same way with the [M3 bolt]{Qty: 12}s. Secure with [M3 nut]{Qty: 12}.

Using 2x [M3 bolt]{Qty: 2} attach the [28BYJ-48]{Qty: 1} by screwing bolts through the arms into the plastic holders. Secure with [M3 nut]{Qty: 2}.

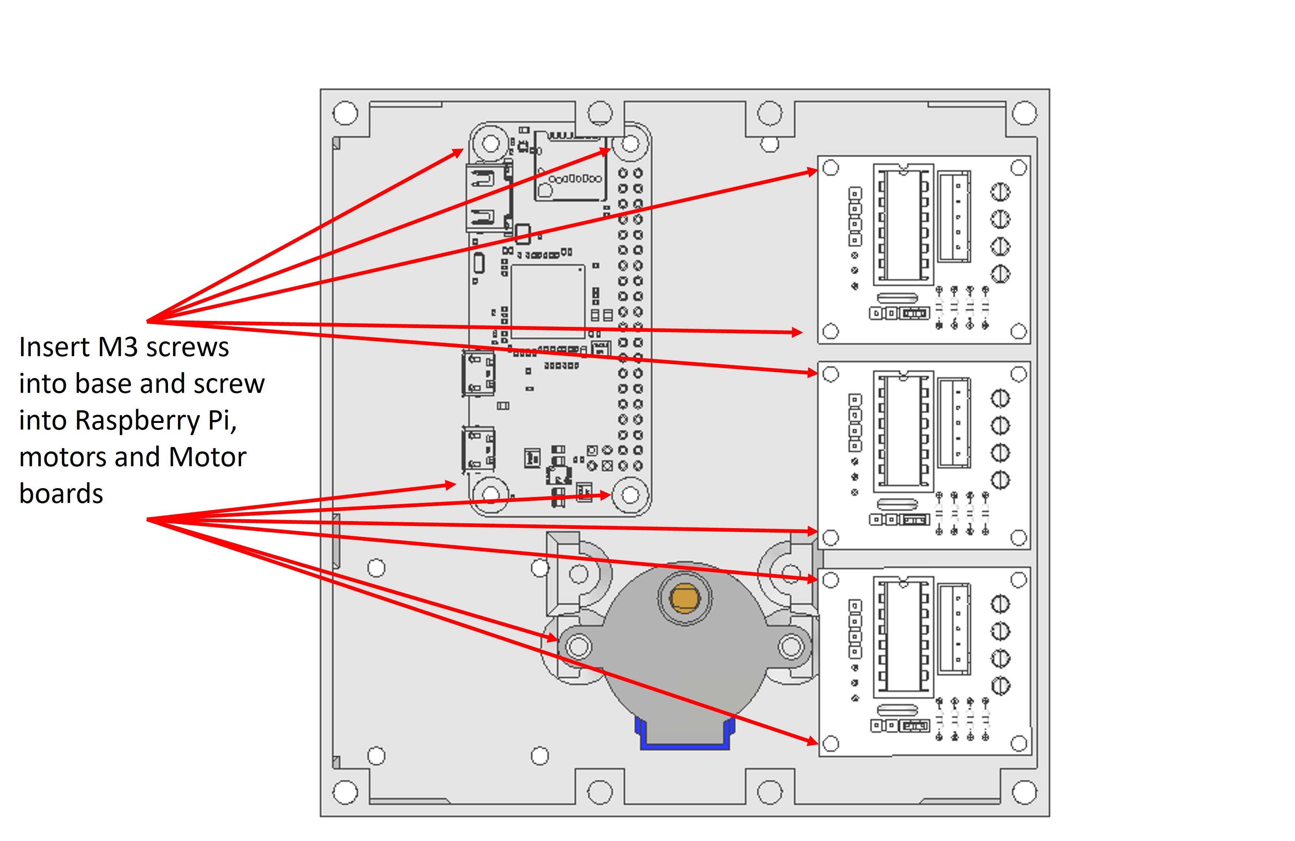
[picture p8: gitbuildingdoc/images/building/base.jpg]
Base instructions


## Motor and motor driver wiring {pagestep}

Attach each [28BYJ-48] header clip to the corresponding [ULN2003] motor driver.

We have had good success powering all of the motors using a simple parallel circuit from the 5V Raspberry Pi pin. Some resources online caution against this, due to concerns that the motors may drain more current than the 5V pin is rated to supply, but personally I have never found any difficulties with this, and it removes the requirement for an additional power source. 

Using [Jumper wires]{Qty: 12} attach each pin of the [ULN2003] to the [Raspberry Pi]. The pin order should be as follows:

* X axis:
    * **Motor pin 1**: Raspberry Pi pin 18
    * **Motor pin 2**: Raspberry Pi pin 23
    * **Motor pin 3**: Raspberry Pi pin 24
    * **Motor pin 4**: Raspberry Pi pin 25

* Y axis:
    * **Motor pin 1**: Raspberry Pi pin 8
    * **Motor pin 2**: Raspberry Pi pin 7
    * **Motor pin 3**: Raspberry Pi pin 12
    * **Motor pin 4**: Raspberry Pi pin 16

* Z axis:
    * **Motor pin 1**: Raspberry Pi pin 4
    * **Motor pin 2**: Raspberry Pi pin 17
    * **Motor pin 3**: Raspberry Pi pin 27
    * **Motor pin 4**: Raspberry Pi pin 22

Please note, if your motors do not move when you test them, you should try to swap motor pin 2 and 3 for each driver. 

## Attaching screw couplings to motors {pagestep}

There are three screw couples; 2x [6mm bolt coupler]{Qty:2} and 1x [3mm bolt coupler]{Qty:1} which are used to attach the [M3x30mm bolt]{Qty:1} and M6 bolts to the [28BYJ-48] motors.

To assemble the screw couplings you should first screw a spare nut all the way along the length of the screw, so that it is flush (or close to flush) with the hex head. You can then insert the hex head into the hexagonal hole in the screw coupler. The nut will help the screw to stay in place in the coupler. 

You can then push the shaft of the [28BYJ-48]{Qty: 2} into the rectangular hole of the screw coupler. 

Once these steps have been completed you should insert 2x [M3 bolt]{Qty:2} into the holes in the side to secure the bolt and shaft from moving. Secure with [M3 nut]{Qty: 2}.

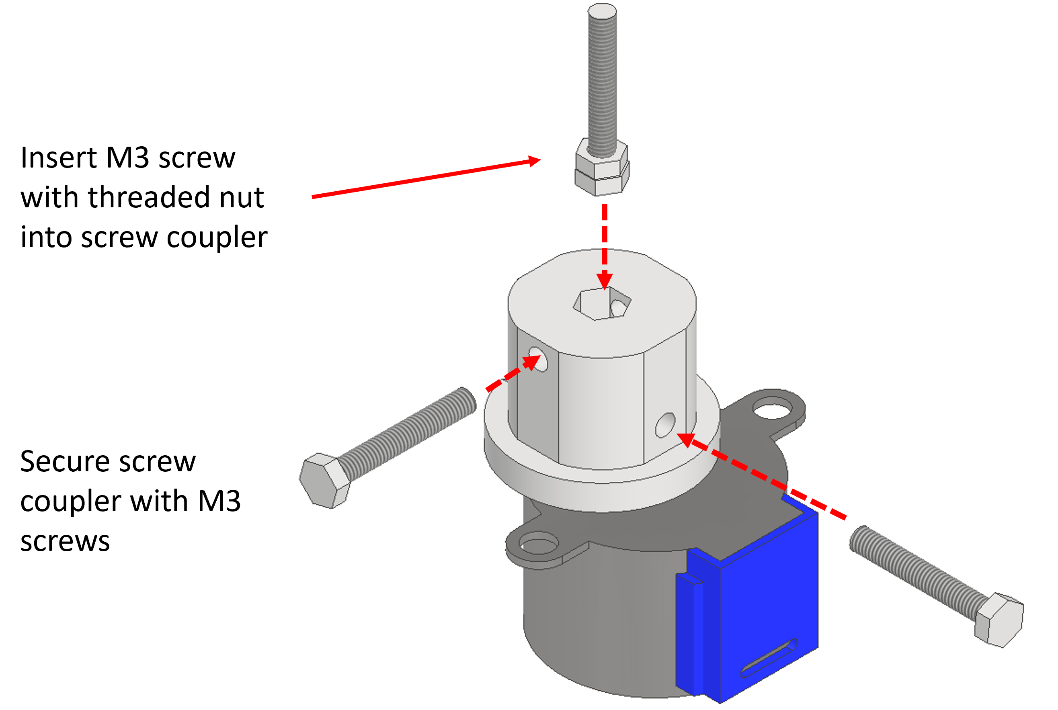
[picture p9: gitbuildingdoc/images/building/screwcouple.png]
Screw coupler


## Assembling Z stage {pagestep}

Insert an [M3 nut]{Qty: 1} into the flexible camera holder. 

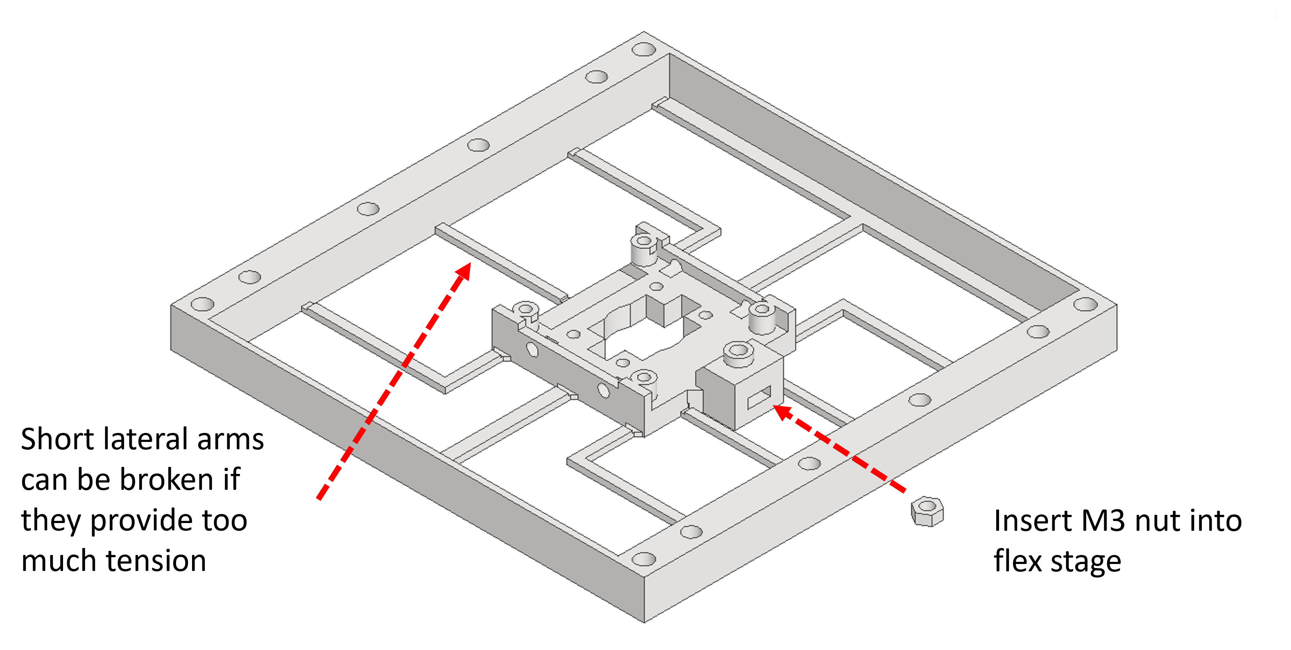
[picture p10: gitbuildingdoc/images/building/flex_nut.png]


## Attaching camera to Z stage {pagestep}

Using 4x [M2.5x6mm bolt]{Qty: 4} Screw the camera onto the flexible holder.

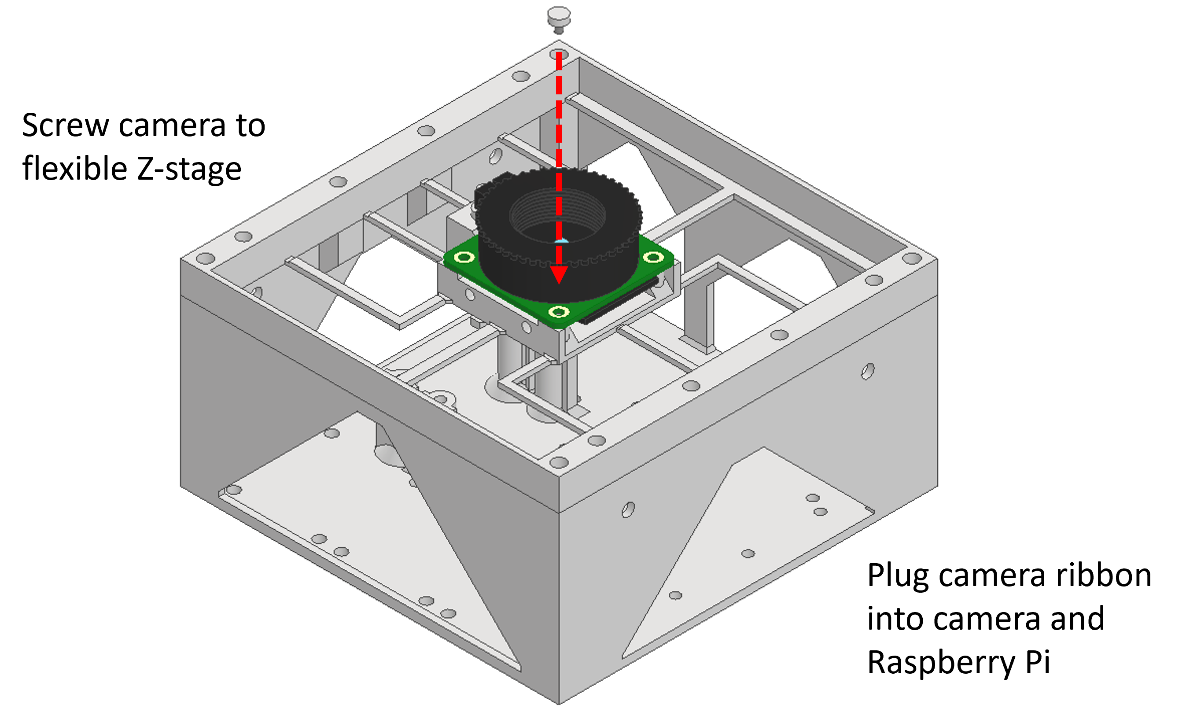
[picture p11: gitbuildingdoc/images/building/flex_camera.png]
Camera holder


You will now need to attach the [Camera ribbon]{Qty: 1}. One end of the camera ribbon will attach to the Raspberry Pi Zero, and the other end will attach to the camera.

## Attaching frame and Z stage to base {pagestep}

Use 4x [M4x10mm bolt]{Qty: 4} to attach the frame to the base. The bolts should screw through the four central holes in the frame, through the camera holder, and into the base. 

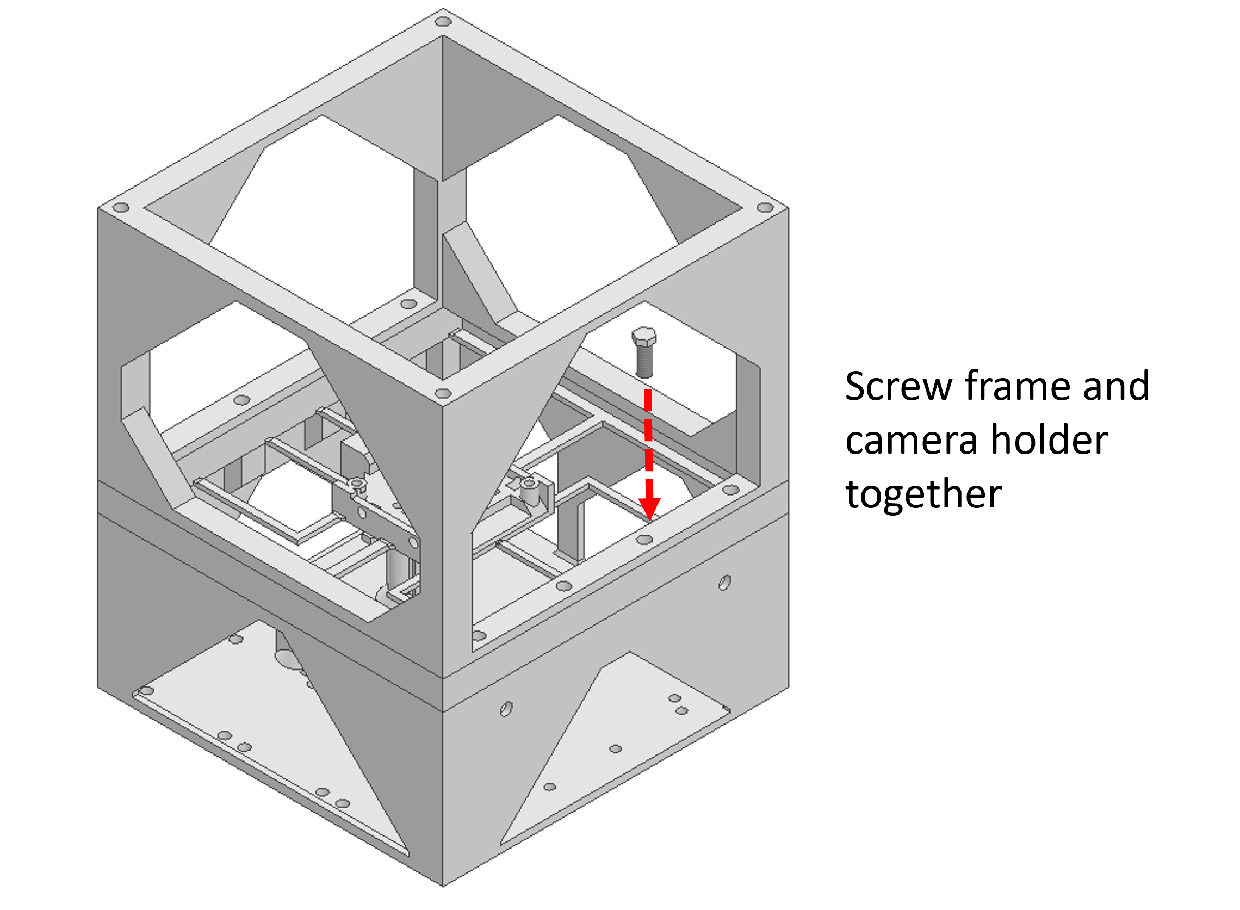
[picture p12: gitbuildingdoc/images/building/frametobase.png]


## Attaching objective tube to camera holder {pagestep}

Use 4x [M3x8mm bolt]{Qty: 4} to attach the objective tube to the camera holder. The bolts screw through the four holes in the bottom of the objective tube arms and into the holes in the camera holder.

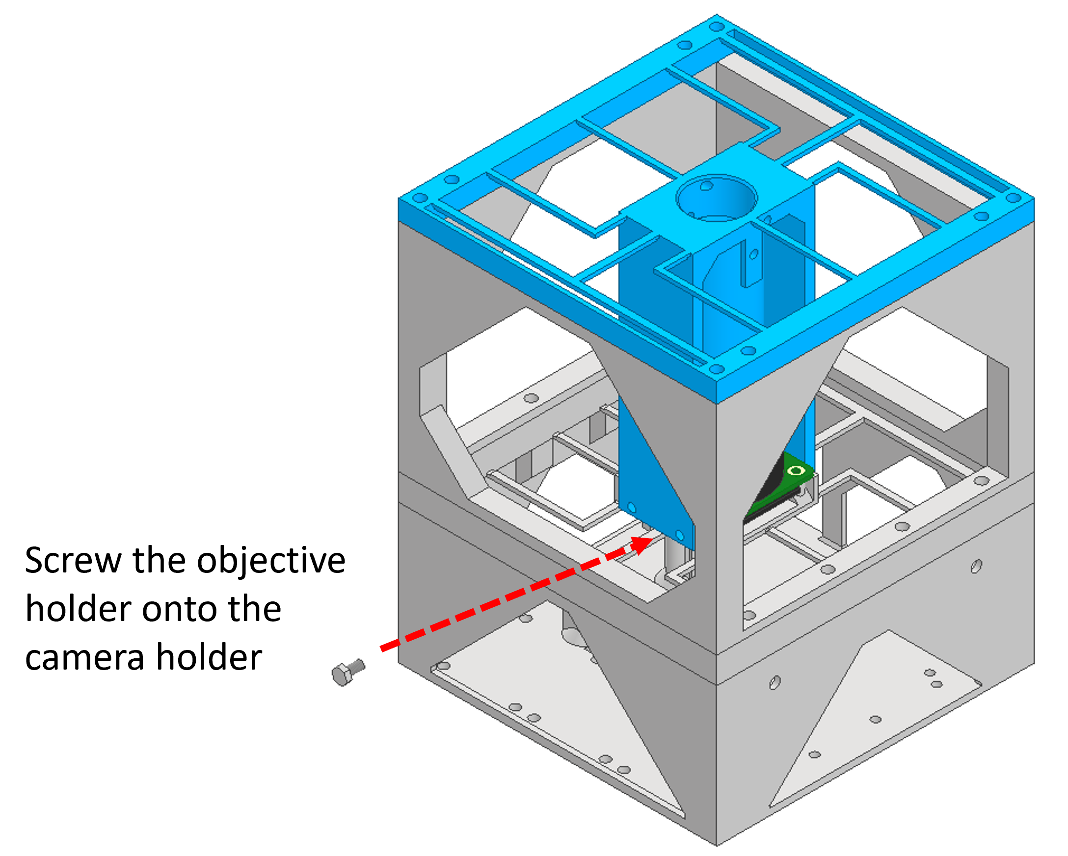
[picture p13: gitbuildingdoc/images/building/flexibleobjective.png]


## Attaching XY stage bottom to objective holder {pagestep}

Use 4x [M4x10mm bolt]{Qty: 4} to attach the X stage bottom to the objective holder.

Slide the X carriage top into the X stage bottom. This should slide directly in, but you may need to slightly bend the part to get the nut holder over the frame.

Insert an [M6 nut]{Qty: 1} into the X carriage. 

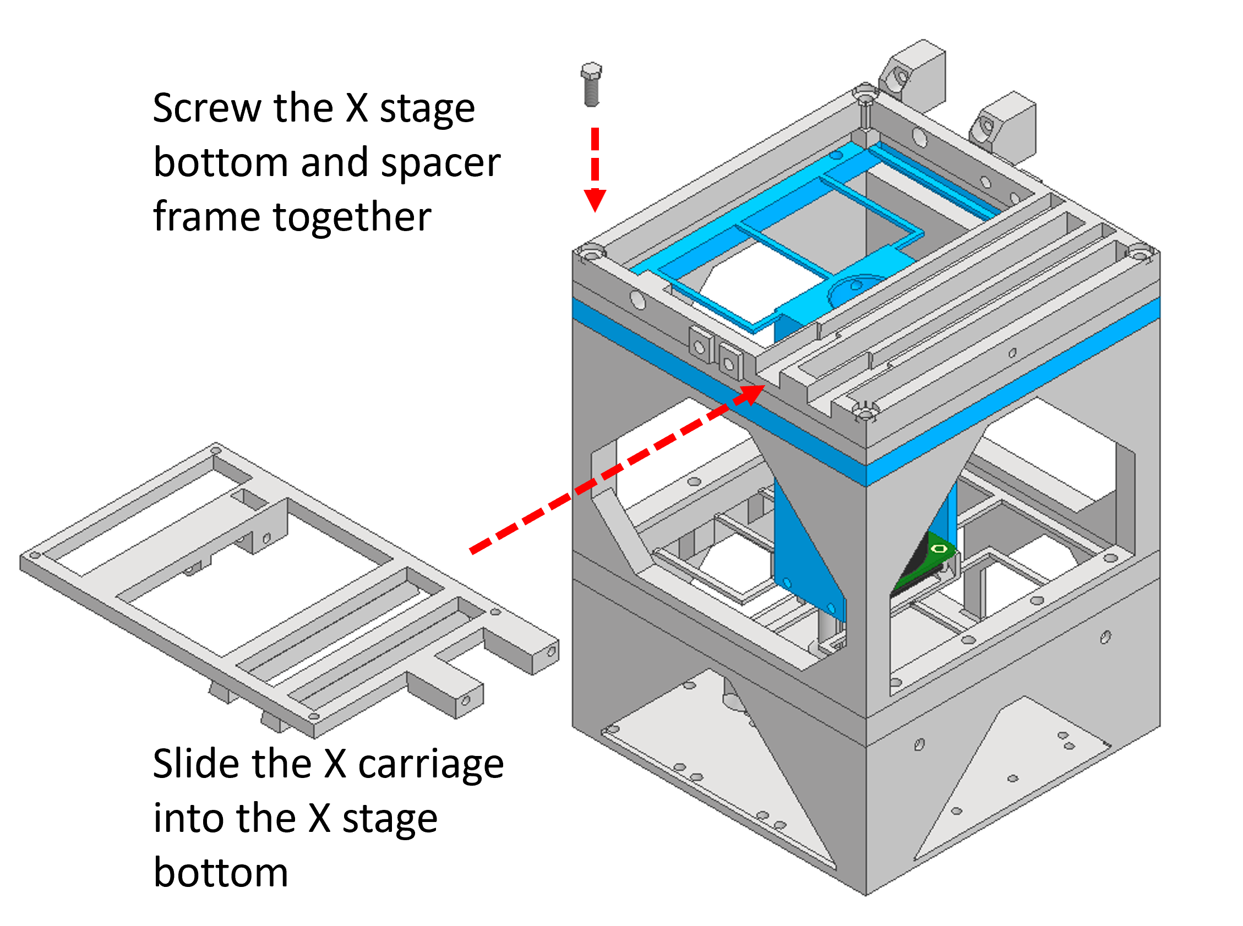
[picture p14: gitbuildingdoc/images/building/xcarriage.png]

 
## Assembling Y stage {pagestep}

Use 4x [M3x8mm bolt]{Qty: 4} to attach the Y stage bottom to the X stage top.

Insert a 2x [M6x130mm bolt]{Qty: 2} into the X and Y stages through the holes in the side of the stage carriages. 

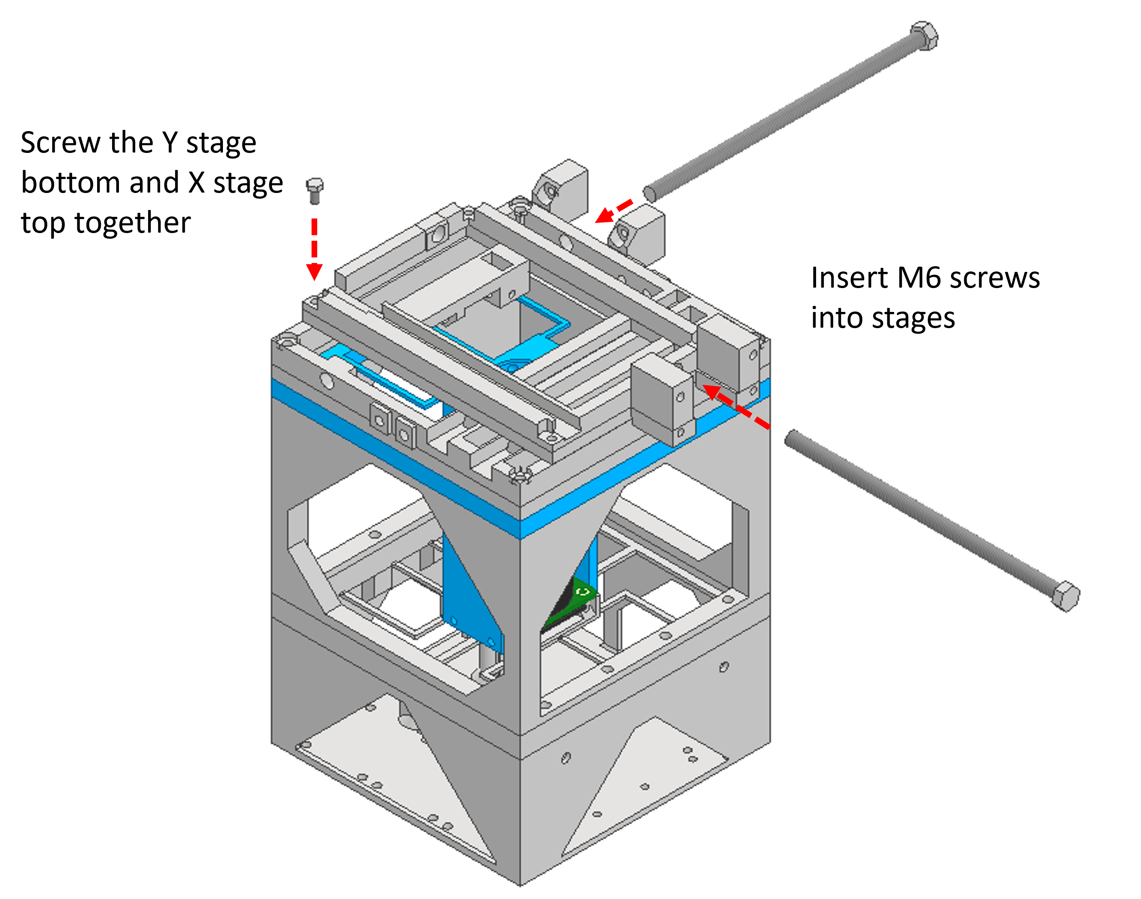
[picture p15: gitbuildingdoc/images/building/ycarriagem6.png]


## Attaching motors Y stage {pagestep}

Use 4x [M3x8mm bolt]{Qty: 4} to attach the [28BYJ-48] motors to the stage.

Slide the Y stage top into the stage. You may need to bend the stage slightly to get the part into the frame. 

Insert a [M6 nut]{Qty: 1} into the Y carriage.

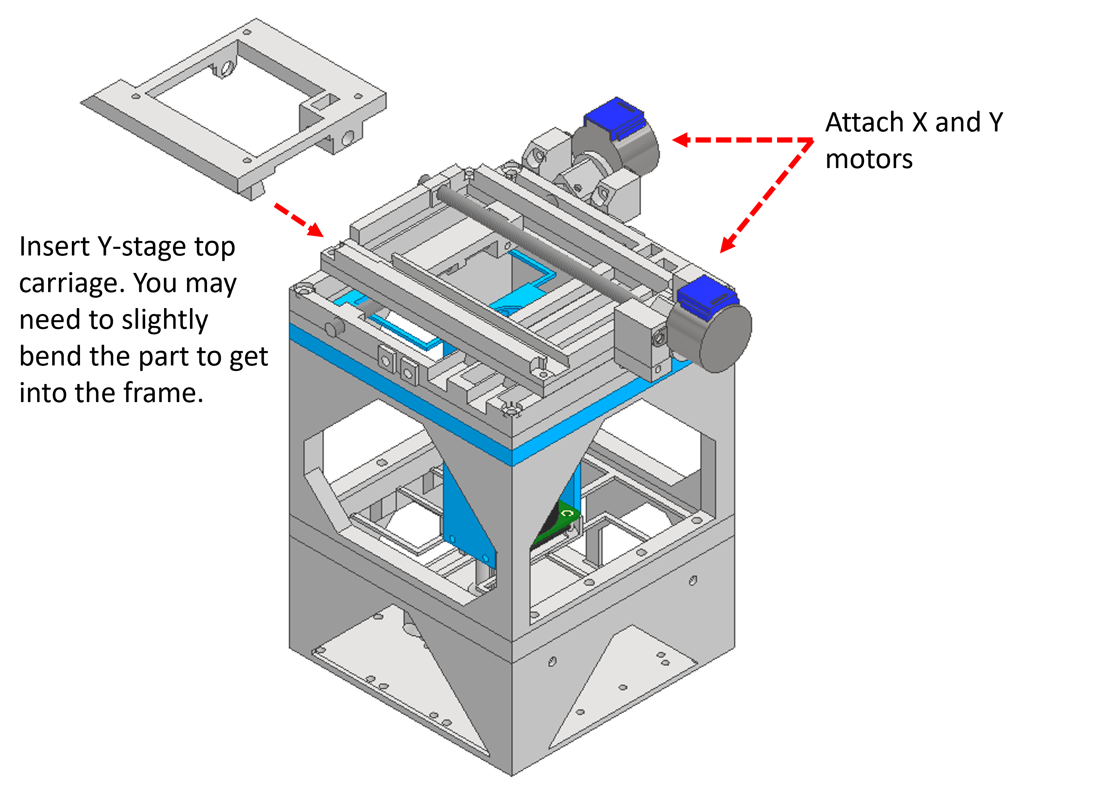
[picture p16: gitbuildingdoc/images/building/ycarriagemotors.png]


## Insert objective {pagestep}

If you are using the [Tube lens], you should insert this into the Tube lens holder. You can then use 1x [M3x8mm bolt]{Qty: 1} inserted into the side of the objective holder to hold the tube lens in place. 

Insert the [RMS objective]{Qty: 1} into the objective holder. It should fit easily in place, but can be held in place using an [M3x8mm bolt]{Qty: 1}.

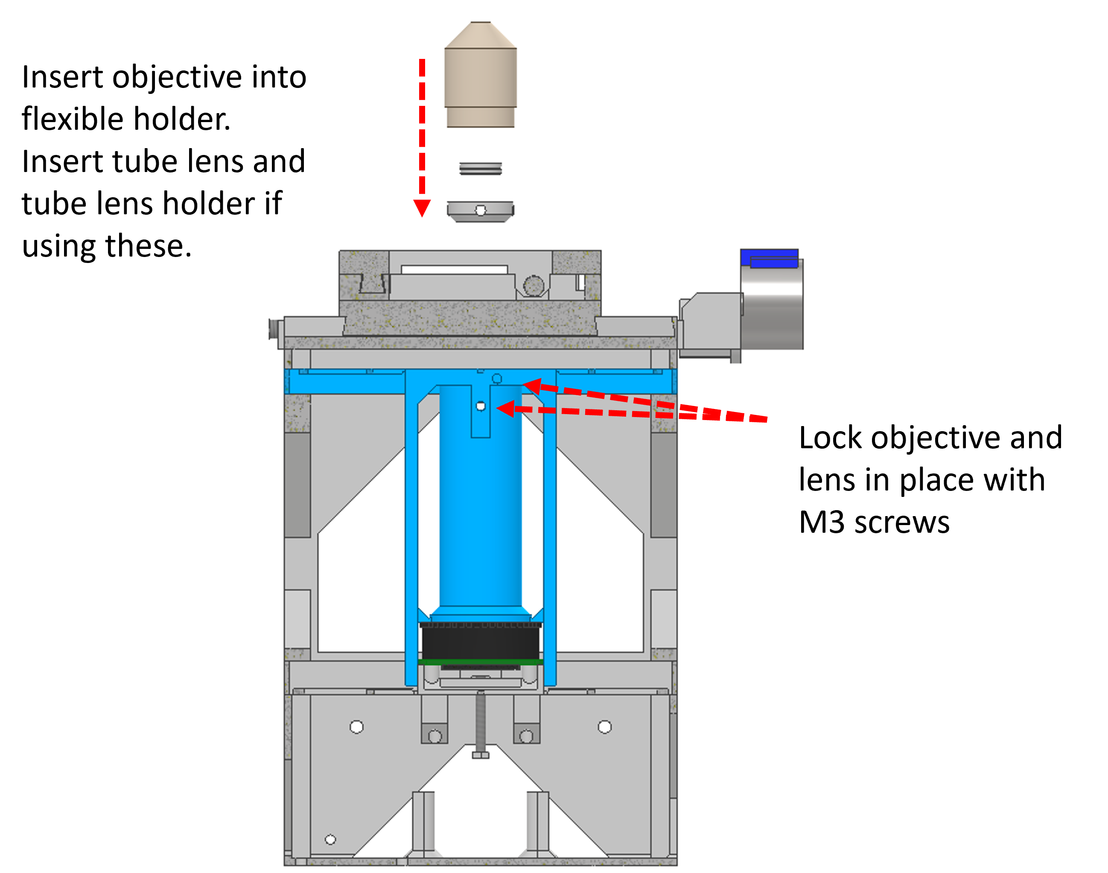
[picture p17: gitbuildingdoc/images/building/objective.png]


## Prepare illumination arm {pagestep}

Glue the [White LED] onto the illumination frame in the central recess.

Insert the [Condenser lens]{Qty: 1} into the condenser holder.

You should prepare the circuit by soldering a 100 ohm [Resistor]{Qty: 1} to 2x [Jumper wires]{Qty: 2}. The jumper wire attached to the positive terminal of the LED should be attached to the 5V pin of the Raspberry Pi. The jumper wire attached to the negative terminal of the LED should be attached to one of the ground pins of the Raspberry Pi. 

Using 2x [M3x8mm bolt]{Qty: 2}, screw the condenser holder onto the illumination frame.

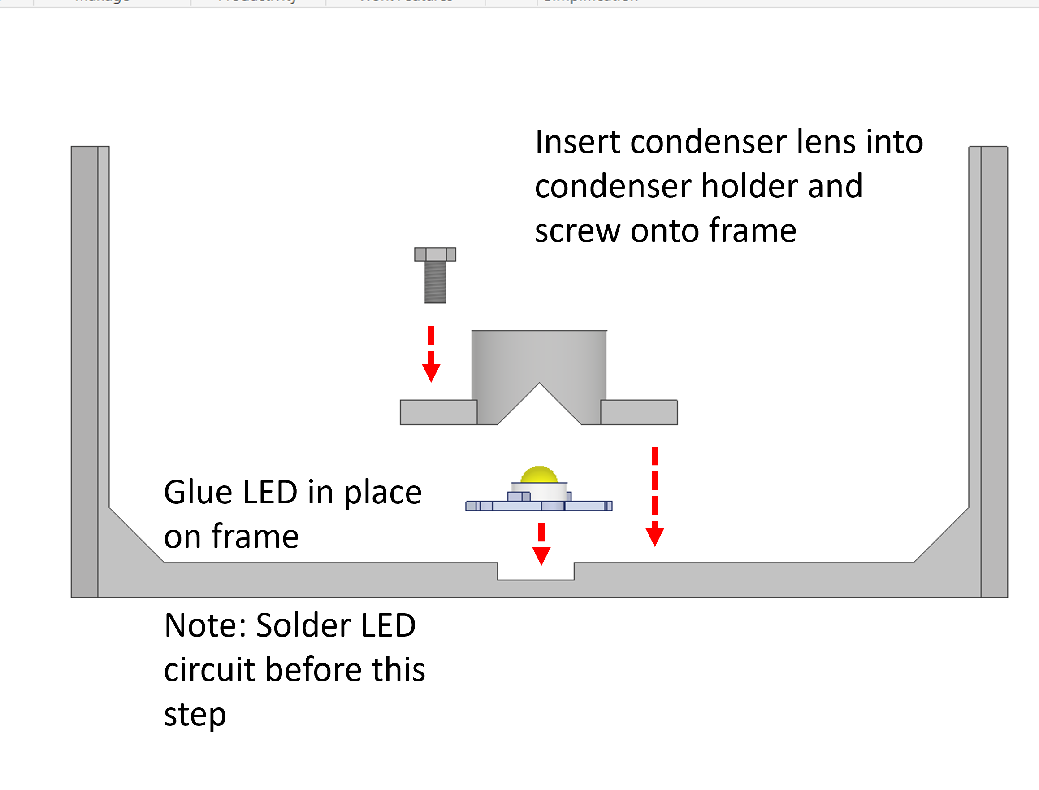
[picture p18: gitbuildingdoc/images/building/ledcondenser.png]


## Attach illumination arm {pagestep}

Use 4x [M4x10mm bolt]{Qty: 4} to attach the illumination frame to the microscope stage.

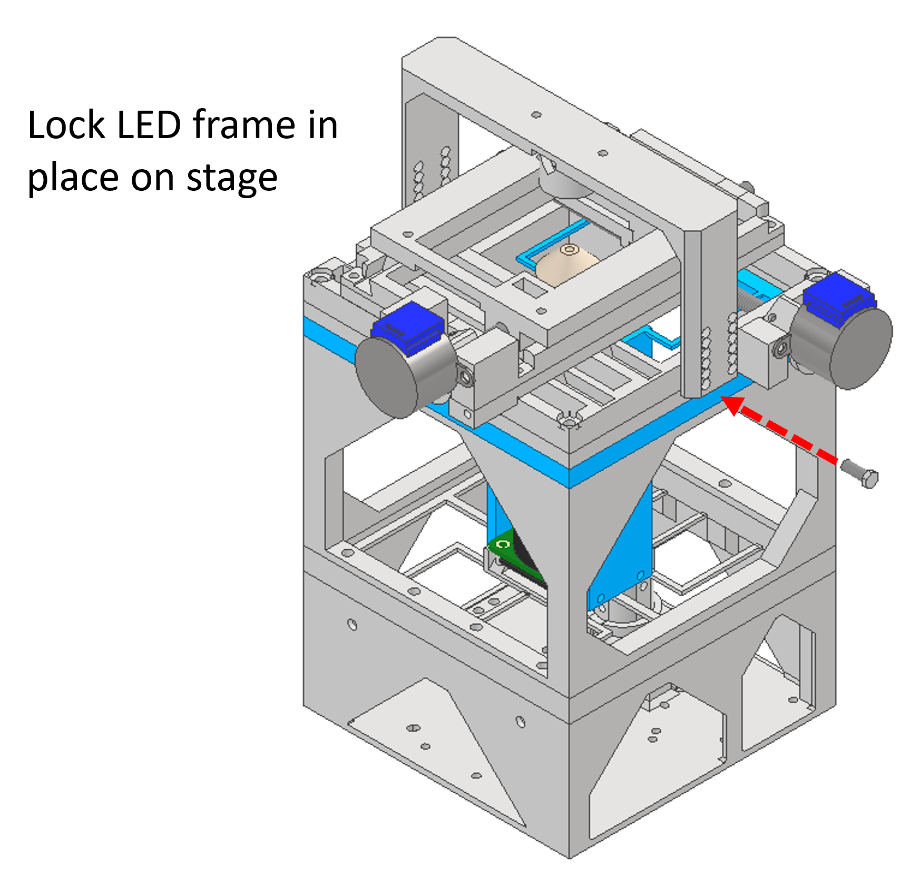
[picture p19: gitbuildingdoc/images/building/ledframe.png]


## Congratulations! {pagestep}

Well done, you have successfully built a microscope! Continue to the next steps for information about using the software.

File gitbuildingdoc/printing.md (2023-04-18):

# Printing parts

## Download the parts {pagestep}

To download the parts, you can either:

1. **(Recommended)** Clone the repository at [https://github.com/Oliverhiggins93/AutomatedSmartphoneMicroscope](https://github.com/Oliverhiggins93/AutomatedSmartphoneMicroscope). All the parts will be located in the cloned folder, in "CAD models/42. Smartphone_inverted_small_v9/stl". 
2. Download the models from the page below by clicking on the links in the STL previews. 

## Print the parts {pagestep}
This is going to be quite a lengthy step, as the microscope requires quite a hefty amount of printing to complete. Each of the parts is designed to be printed on a basic PLA extrusion printer without support. Personally I have had good success printing the parts with a standard 0.4mm nozzle on an Ender 3 printer in PLA.

Each of our microscopes have been sliced using the standard quality (0.2mm layer height, 20% infill) settings in Ultimaker Cura. The total print time for all parts was just under 40 hours and required several separate prints because of the size of the part footprint. 

The full list of all parts to print is as follows:

1. Base (Bottom_carriage) x 1
Base (Bottom_carriage)
2. Camera holder (Flexible_cam_holder) x 1
Camera holder (Flexible_cam_holder)
3. Frame (160mm_shunt_box) x 1
Frame (160mm_shunt_box)
4. Objective tube (Flexible_tube_bolster_fixed_v3) x 1
Objective tube (Flexible_tube_bolster_fixed_v3)
5. X Stage base (Rail_stage_x_m6) x 1
X Stage base (Rail_stage_x_m6)
6. X Stage top (Rail_carriage_v2) x 1 
X Stage top (Rail_carriage_v2)
7. Y stage bottom (Rail_stage_y_v1.stl) x 1
Y stage bottom
8. Y stage top (Rail_carriage_y_top_v2.stl) x 1
Y stage top
9. Shaft couple 3mm (3mm_shaft_couple_sideclip_v4.stl) x 1
Shaft couple 3mm
10. Shaft couple 6mm (6mm_shaft_couple_sideclip_v2.stl) x 2
Shaft couple 6mm
11. LED frame (Led_frame_2_4mm.stl) x 1
LED frame
12. Tube lens holder x 1
Tube lens holder
13. Condenser holder frame (Condenser_holder_frame.stl) x 1
Condenser holder

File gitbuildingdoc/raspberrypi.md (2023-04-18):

[SD card]:Parts.yaml#SDCard

# Raspberry Pi Software

A software image for the Raspberry Pi will be available soon which can be burned directly.  

Currently the easiest way to set up your Raspberry Pi to stream to your smartphone is as follows:

* Flash your [SD card]{Qty: 1} with the latest version of Raspbian. 
* Open a terminal window
* Clone the repository by running command:
    * cd ~
    * git clone https://github.com/Oliverhiggins93/AutomatedSmartphoneMicroscope.git
* Add the Raspberry Pi server script to rc.local to schedule running at startup. Typing the following in to the terminal:
    * sudo nano /etc/rc.local
    * Add the following line before "exit 0":
        * sudo python3 /~/AutomatedSmartphoneMicroscope/Raspberry_pi/stills_server.py &

* Add your phone hotspot as a WiFi connection to join:
    * Open a terminal window and enter the following:
        * sudo nano /etc/wpa_supplicant/wpa_supplicant.conf
    * Copy-paste the following into the wpa_supplicant.conf file: 

>i country=gb </br>
>i update_config=1 </br>
>i ctrl_interface=/var/run/wpa_supplicant </br>
>i
>i network={ </br>
>i    scan_ssid=1 </br>
>i    ssid="microscope" <br>
>i    psk="smart" <br> 
>i }

>! **Security warning**
>!
>! Here we are suggesting to use a default SSID and password. This will mean that you will need to change the SSID of your phone so that the Raspberry Pi can pair to your phone. This is convenient because each smartphone user can change their hotspot ssid and password relatively quickly without having to interface with a screen. If you are worried about changing your smartphone's hotspot SSID and password to something that may be less secure, I would suggest you can change the ssid or psk field to the default for your smartphone. 

* Reboot. Upon reboot your Raspberry Pi will start looking to join the mobile hotspot of your smartphone, and as long as the camera has been correctly connected, the script will begin streaming images.

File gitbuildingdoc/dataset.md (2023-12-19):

# Dataset of Helminth egg images

The dataset contains over 12,000 annotated images of helminth eggs in Kato-Katz faecal stains. The annotations were confirmed by expert parasitologists at the Ministry of Health Uganda, Vector Control Division, Kampala. 

Six common helminth species are represented in the dataset: 

* Schistosoma mansoni 
* Trichuris trichiura
* Hookworm
* Ascaris lumbricoides
* Hymenolepis nana
* Taenia solium 

The dataset can be found on Kaggle: [Helminth dataset](https://www.kaggle.com/datasets/oliverjackhiggins/helminth-image-dataset)

Further information about the preparation of the dataset, and the subsequent analysis of the trained model can be found in the PhD thesis.

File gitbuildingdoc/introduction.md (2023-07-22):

#Introduction and project rationale

This project forms a large part of a PhD project which was aiming to automate the reading of Kato-Katz fecal smears for the identification and diagnosis of soil transmitted helminth (STH) infections. Helminths are parasitic worms which often infect people in areas of poor sanitation. The project uses a smartphone to control the microscope and analyse images for the presence of parasite eggs. 

#How is this different from other microscopy projects?

Much of the inspiration from this project comes from the OpenFlexure Microscope, which is a fantastic open hardware project developed by the Bath Open INstrumentation Group (BOING). I highly recommend viewing their webpage, as they have created several innovations to improve open hardware projects (including GitBuilding which these documentation pages were built with). 

[OpenFlexure webpage](https://openflexure.org/).

There are a few differences between this project and the OpenFlexure Microscope. The primary differences are that our microscope does not use flexure for the X and Y movement, and that our control software uses a separate app on the smartphone rather than using the Raspberry Pi directly. The decision to move away from flexures was to try to increase the speed and range of movement for the X and Y dimensions, which we hoped would allow us to scan large samples more quickly. The use of a smartphone was to try to remove the need for additional screens and peripherals (such as keyboards and mice) to keep the microscope device highly portable.

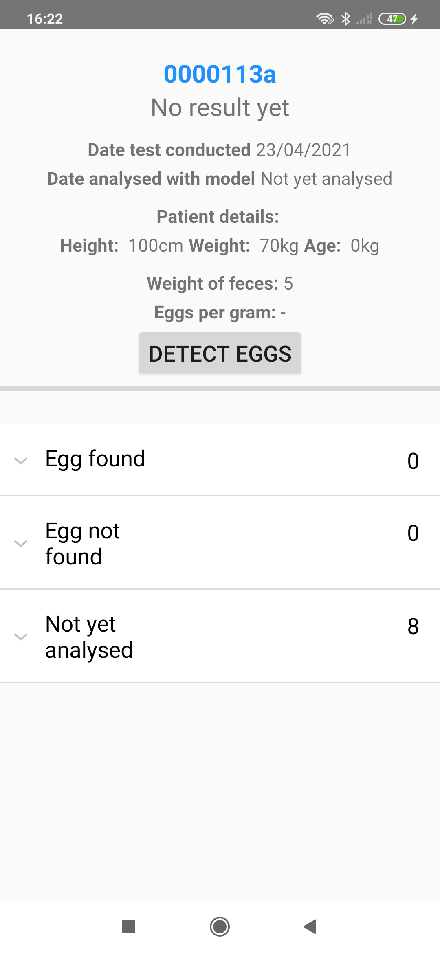
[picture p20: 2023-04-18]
gitbuildingdoc/images/appinstructions/detecteggs.jpg

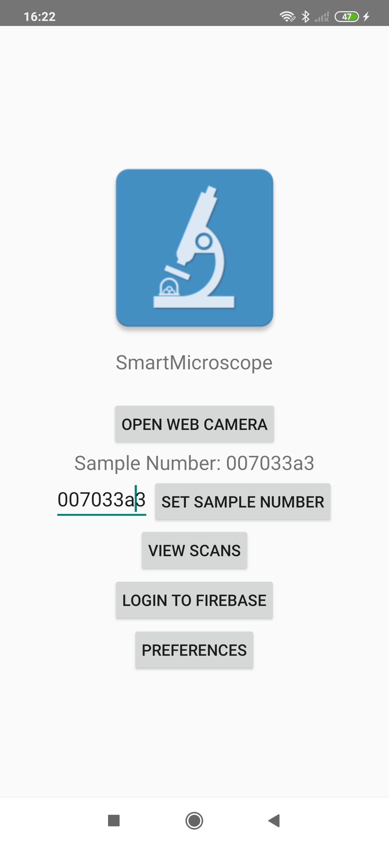
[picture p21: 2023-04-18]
gitbuildingdoc/images/appinstructions/mainmenu.jpg

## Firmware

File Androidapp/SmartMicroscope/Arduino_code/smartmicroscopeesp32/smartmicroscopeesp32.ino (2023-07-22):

//This example code is in the Public Domain (or CC0 licensed, at your option.)
//By Evandro Copercini - 2018
//
//This example creates a bridge between Serial and Classical Bluetooth (SPP)
//and also demonstrate that SerialBT have the same functionalities of a normal Serial

#include "BluetoothSerial.h"
#include "Stepper.h"

#if !defined(CONFIG_BT_ENABLED) || !defined(CONFIG_BLUEDROID_ENABLED)
#error Bluetooth is not enabled! Please run `make menuconfig` to and enable it
#endif

BluetoothSerial SerialBT;


String readString;
String stepType;
String stepMagnitude;
Stepper motorx = Stepper(2048, 15, 2, 4, 16); //pins here refer to eps32 numbering on board surface. If not working try swapping pins connected to in2 and in3.
Stepper motory = Stepper(2048, 13, 12, 14, 27);
Stepper motorz = Stepper(2048, 26, 25, 33, 32);
int led = 18;
int brightness = 250;

void setup() {
  Serial.begin(115200);
  SerialBT.begin("SmartMicroscope"); //Bluetooth device name
  Serial.println("The device started, now you can pair it with bluetooth!");
  motorx.setSpeed(14);
  motory.setSpeed(14);
  motorz.setSpeed(14);
  ledcAttachPin(led, 0);
  ledcSetup(0, 5000, 8);
  ledcWrite(0, 0);
  
}

void loop() {
  
  
  if (Serial.available()) {
    SerialBT.write(Serial.read());
  }
  
  if (SerialBT.available()) {
    readString = SerialBT.readString();
    Serial.print("Received:");
    Serial.println(readString);
    ledcWrite(0, brightness);

    if (readString.length() > 3){
      if (readString.substring(0,3) == "mrx") {
        int len = readString.length();
        int integerStep = readString.substring(4,len).toInt();
         
        Serial.println(readString);
        Serial.println(integerStep);
        motorx.step(integerStep);
        Serial.println("Steps complete");
        }

      else if (readString.substring(0,3) == "mry") {
        int len = readString.length();
        int integerStep = readString.substring(4,len).toInt();
         
        Serial.println(readString);
        Serial.println(integerStep);
        motory.step(integerStep);
        Serial.println("Steps complete");
        }

      else if (readString.substring(0,3) == "mrz") {
        int len = readString.length();
        int integerStep = readString.substring(4,len).toInt();
         
        Serial.println(readString);
        Serial.println(integerStep);
        motorz.step(integerStep);
        Serial.println("Steps complete");
        }

      else if (readString.substring(0,3) == "led") {
        int len = readString.length();
        brightness = readString.substring(4,len).toInt();
          if (brightness <= 0 || brightness >= 255) {
            brightness = 255;
            }
        Serial.println(readString);
        }

    
  }
  }
        delay(1);
}

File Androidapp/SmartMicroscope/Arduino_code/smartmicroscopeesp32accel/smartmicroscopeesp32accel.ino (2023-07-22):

 //This example code is in the Public Domain (or CC0 licensed, at your option.)
//By Evandro Copercini - 2018
//
//This example creates a bridge between Serial and Classical Bluetooth (SPP)
//and also demonstrate that SerialBT have the same functionalities of a normal Serial

#include "BluetoothSerial.h"
#include "AccelStepper.h"

#if !defined(CONFIG_BT_ENABLED) || !defined(CONFIG_BLUEDROID_ENABLED)
#error Bluetooth is not enabled! Please run `make menuconfig` to and enable it
#endif

BluetoothSerial SerialBT;


String readString;
String stepType;
String stepMagnitude;
int len;
int integerStep;
//Stepper motorx = Stepper(2048, 15, 2, 4, 16); //pins here refer to eps32 numbering on board surface. If not working try swapping pins connected to in2 and in3.
//Stepper motory = Stepper(2048, 13, 12, 14, 27);
//Stepper motorz = Stepper(2048, 26, 25, 33, 32);

AccelStepper motorx(AccelStepper::FULL4WIRE, 15, 4,2, 16); //hq currently has 2 and 4 wrong way around 
AccelStepper motory(AccelStepper::FULL4WIRE, 13, 12,14, 27); 
AccelStepper motorz(AccelStepper::FULL4WIRE, 26, 25, 33, 32);

int led = 18;
int brightness = 250;

void setup() {
  Serial.begin(115200);
  SerialBT.begin("SmartMicroscope2"); //Bluetooth device name
  Serial.println("The device started, now you can pair it with bluetooth!");

  motorx.setMaxSpeed(325);
  motory.setMaxSpeed(325);
  motorz.setMaxSpeed(325);
  motorx.setSpeed(300);
  motory.setSpeed(300);
  motorz.setSpeed(300);
  
  motorx.setAcceleration(300);
  motory.setAcceleration(300);
  motorz.setAcceleration(300);
  
  ledcAttachPin(led, 0);
  ledcSetup(0, 5000, 8);
  ledcWrite(0, 0);
  
}

String getStringPartByNr(String data, char separator, int index) {
    int stringData = 0;        //variable to count data part nr 
    String dataPart = "";      //variable to hole the return text

    for(int i = 0; i<data.length()-1; i++) {    //Walk through the text one letter at a time
        if(data[i]==separator) {
            //Count the number of times separator character appears in the text
            stringData++;
        } else if(stringData==index) {
            //get the text when separator is the rignt one
            dataPart.concat(data[i]);
        } else if(stringData>index) {
            //return text and stop if the next separator appears - to save CPU-time
            return dataPart;
            break;
        }
    }
    //return text if this is the last part
    return dataPart;
}

void loop() {
  
  motorx.run();
  motory.run();
  motorz.run();
  
  //if (Serial.available()) {
    //SerialBT.write(Serial.read());
  //}
  if (SerialBT.available()) {
    readString = SerialBT.readString();
    //Serial.println("Received:" + readString);
    //ledcWrite(0, brightness);
    
    if (readString.length() > 3){
      if (readString.substring(0,2) == "mr") {
        len = readString.length();
        integerStep = readString.substring(4,len).toInt();
        
        if (readString.substring(0,3) == "mrx"){
          motorx.moveTo(integerStep);
        }
        else if (readString.substring(0,3) == "mry"){
          motory.moveTo(integerStep);
        }
        else if (readString.substring(0,3) == "mrz"){
          motorz.moveTo(integerStep);
        }
      }


      else if (readString.substring(0,2) == "ma") {

        String xstring = getStringPartByNr(readString, ',', 0);
        int xlen = xstring.length();
        int xStep = xstring.substring(4,xlen).toInt();
        
        String ystring = getStringPartByNr(readString, ',', 1);
        int ylen = ystring.length();
        int yStep = ystring.substring(4,ylen).toInt();
        
        String zstring = getStringPartByNr(readString, ',', 2);
        int zlen = zstring.length();
        int zStep = zstring.substring(4,zlen).toInt();
        
        Serial.println(xStep);
        Serial.println(yStep);
        Serial.println(zStep);
        motorx.moveTo(xStep);
        motory.moveTo(yStep);
        motorz.moveTo(zStep);
      }
      
      
      else if (readString.substring(0,3) == "led") {
          len = readString.length();
          brightness = readString.substring(4,len).toInt();
          if (brightness <= 0 || brightness >= 255) {
              brightness = 255;
              }
          Serial.println(readString);
          }

        else if (readString.substring(0,2) == "po") {
        len = readString.length();
        int pos = readString.substring(4,len).toInt();
        if (readString.substring(0,3) == "pox"){
          motorx.setCurrentPosition(pos);
        }
        if (readString.substring(0,3) == "poy"){
          motory.setCurrentPosition(pos);
        }
        if (readString.substring(0,3) == "poz"){
          motorz.setCurrentPosition(pos);
        }
        Serial.println(readString);
        }
        
        else if (readString.substring(0,3) == "zer") {
          motorx.setCurrentPosition(0);
          motory.setCurrentPosition(0);
          motorz.setCurrentPosition(0);
          Serial.println(readString);
        }
        else if (readString.substring(0,3) == "ori") {
          motorx.moveTo(0);
          motory.moveTo(0);
          motorz.moveTo(0);
          Serial.println(readString);
        }
  }
  }
}

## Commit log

2022-09-09 First commit for file system
    [160mm_shunt_box.ipt, 28BYJ-48 Stepper.ipt, 3mm_shaft_couple_sideclip_v4.ipt, 6mm_shaft_couple_sideclip_v2.ipt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]
2022-09-09 Changed location of gitbuilding docs
    [index_BOM.csv]
2022-09-21 add stls
    [160mm_shunt_box.stl, 1W_star_LED.SLDPRT, 3mm_shaft_couple_sideclip_v4.stl, 6mm_shaft_couple_sideclip_v2.stl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]
2023-04-18 Changes to documentation
    [28BYJ-48 Stepper.ipt, 6mm_shaft_couple_sideclip_v2.ipt, Condenser_holder_frame.stl, Flexible_tube_bolster_fixed_v3.ipt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]
2023-04-18 rebuild pages 2
    [160mm_shunt_box.stl, 3mm_shaft_couple_sideclip_v4.stl, 6mm_shaft_couple_sideclip_v2.stl, Bottom_carriage.stl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]
2023-04-18 Changes to docs
    [160mm_shunt_box.stl, 3mm_shaft_couple_sideclip_v4.stl, 6mm_shaft_couple_sideclip_v2.stl, Bottom_carriage.stl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]
2023-12-19 changes to docs to add dataset page
    [160mm_shunt_box.stl, 3mm_shaft_couple_sideclip_v4.stl, 6mm_shaft_couple_sideclip_v2.stl, Bottom_carriage.stl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]
